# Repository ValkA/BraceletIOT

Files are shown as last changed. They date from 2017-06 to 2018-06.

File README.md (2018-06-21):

# Bracelet 101
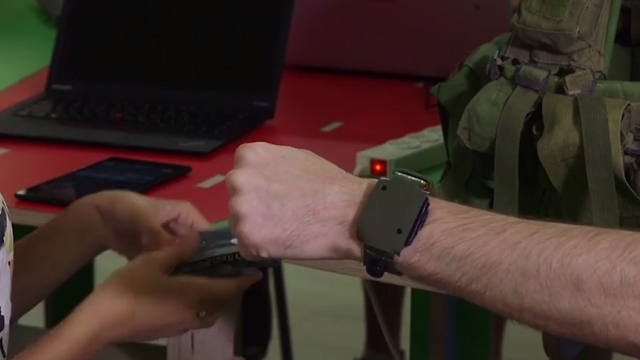
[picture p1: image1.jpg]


This is the repository of "Bracelet 101", a POC of smart bracelet for Medical Corps that is attached to an injured person in order to record medical events (i.e injection of morphine, wearing a tourniquet etc...).

The bracelet uses NFC to register events in the field and Bluetooth to communicate later with an Android device that is held by a doctor at hospital or at the battalion aid station.

Each medical treatment has an NFC tag with the id of the treatment and should be registered in the bracelet by holding it near the bracelet before giving the treatment to the injured person.

## Media:
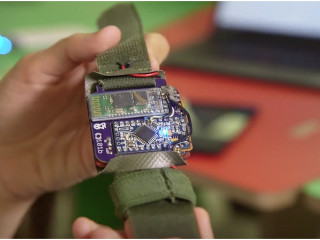
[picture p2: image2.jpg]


Israel Hayom article - http://www.israelhayom.co.il/article/565423/

YNet Health article - https://www.ynet.co.il/articles/0,7340,L-4991215,00.html

Israeli Channel 10 article - http://192.118.60.6/radioMP4/2017/07/25/7880181.mp4

Technion Israel Institute of Technology Facebook page - https://www.facebook.com/Technion.Israel/videos/1805491129468339/

## Bluetooth protocol:
The bracelet reads commands via Bluetooth serial in the format <$type,$data>.

After receiving a command, the bracelet sends '#' as an ack. If there wasn't enough memory to add a record, __the bracelet will send '!' back__, instead of '#'.

The following types can be sent to the bracelet:

- <0,Integer> adds a tag scan. In case the doctor wants to add a treatment manually through the phone.
$data is the treatment number.

- <2,Integer> - adds new data (such as temperature measurement by doctor).

- <3,$time,$tsid,Integer> - update record [$time,$tsid] with new data (Integer 14bit max)

- <4,Integer> - adds a record of headquarters communication (such as evacuation notification),
$data can be any kind of Integer.

- <5,Integer> - adds a record of blood pressure.
$data = blood pressure

- <6,Integer> - Turns on buzzer,
$data has no meaning, but should be some kind of Integer. 0 can be put there.

- <7,$time,$tsid,0> - delete record represented by $time,$tsid.

- <8,Integer> - adds soldierID record. $data should contain the soldier's personal number.

- <13,Integer> - adds soldier status (severity of injury).
$data is id of the status.

For example, the command <1,123> will add a record into the bracelet that represents a new connection by a phone that is represented by the number 123. As a response you will get the database.

#### Special commands:

- LOCATION:
To register location you should send <10,(double/float)latitude><11,(double/float)longitude>
you will see the location when you will send <1,doctor_id>. the location will be among the tags in the container.
for example, [<1,3,0,1><10,32.2343><11,7.23456>]. fields 2 and 3 represent the latitude and longitude.

- SYNC:
<14,Integer> - a special record that can be used to keep the Android and the bracelet in sync.
When the bracelet receives this record, it sends the entire database back, but __does not place this record in it's database__.
The format of the database is the same as in <1, Integer>.
This allows this record to be sent periodically from Android to the bracelet to make sure they are both in sync (for example, every 30 seconds).
Similar to <6, Integer> the $data here has no meaning, but should be some kind of Integer.

- DOCTOR CONNECTION:
<1,Integer> on connection this is the first thing should be sent to the bracelet.
$data represents a unique number of the phone.
As an acknowledgement the bracelet will send back its database with the following format:
[<$type,$time,$tsid,$data>, <$type,$time,$tsid,$data>, ..., <$type,$time,$tsid,$data>]
also the format <3,$time,$tsid,$pointer_time,$pointer_tsid,$data> may be in the container,
which represents an update record (that was added with <3,$time,$tsid,Integer> message from doctor)
(records can be tags, app_data or any other things as defined in this doc https://docs.google.com/document/d/1-qHOoyWK5xLiwJvJ40AK0ONJ1xDmyQk-YbECwnUxzqk/edit)

## NFC Protocol (Tag format):
The tags scanned by the bracelet must be in one of the following 2 formats:
- Integer String

For example: 50 Optalgin 10mg

This format is used for different treatments. It's supposed to be in an NFC tag attached to the treatment item, to be scanned by the bracelet.

- dInteger String

For example: d1234567 Israel Israeli

This format is for the soldier personal number. It's supposed to be in an NFC tag attached to the soldier's tag (diskit).

Notice that in both cases __only the number is scanned by the bracelet__. The following string is completely ignored. It is there __optionally__ so that it could be used in other devices.

The Integer must be smaller than 2^28, which is the maximum number that can be saved in the bracelet (28 bits are stored for each record's data).

## Debugging:
It is possible to send debugging commands to the Arduino through the Serial (physical connection to the PC). There are currently 3 types of debugging commands:
- d - print the current database to the Serial.
- m - print memory information to the Serial (number of records currently stored)
- <$type,$data> - add a specific record to the Arduino. The record would be parsed in the exact same manner as a record sent to the Arduino from Bluetooth. If the record is not recognized as one of the above legal records, you'll get an error and the record would not be added.

The Arduino also sends debugging information to the Serial during normal operation, such as detailed error messages. Therefore, if you encounter unexpected behaviour when interfacing through Bluetooth, connect the Arduino through the serial to see detailed debug messages.

## Wiring:
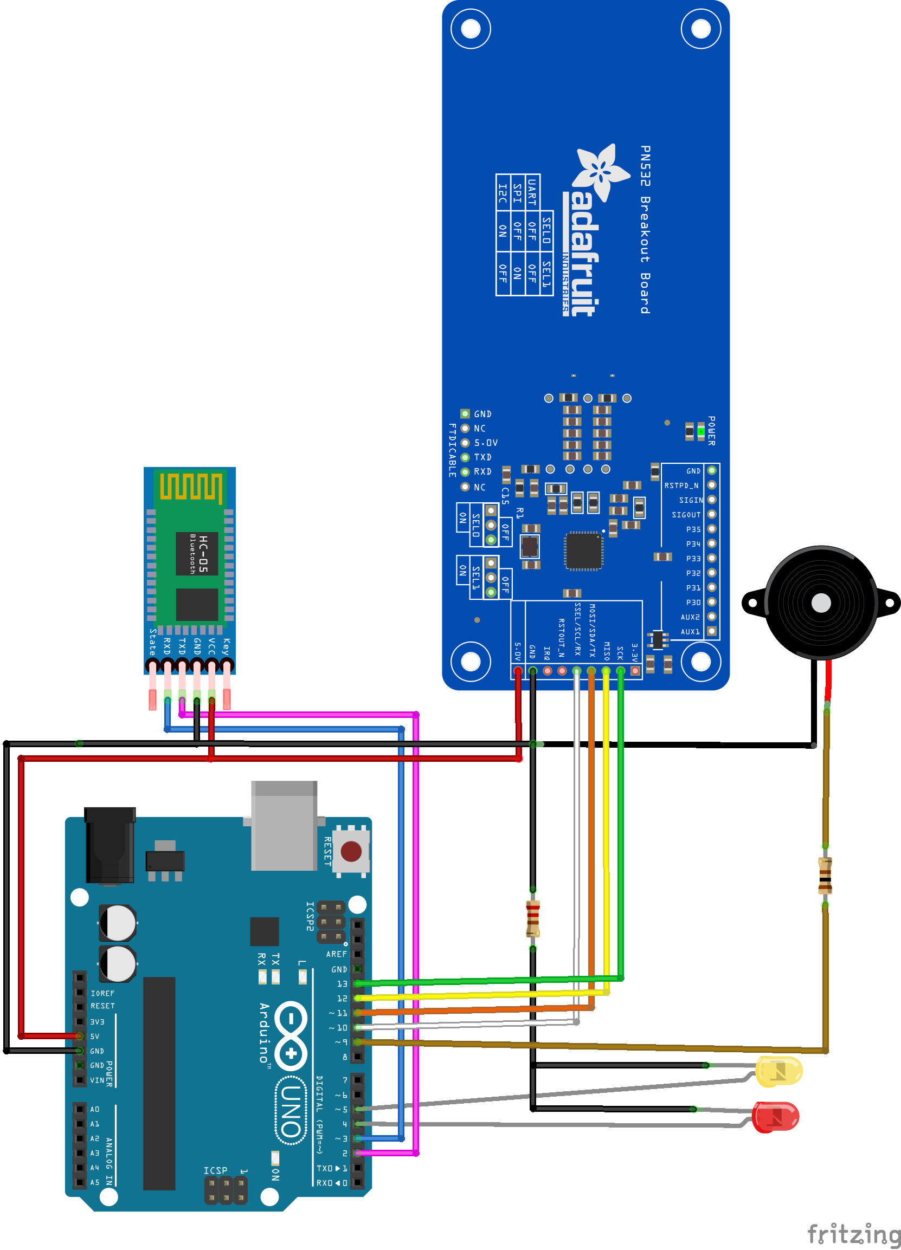
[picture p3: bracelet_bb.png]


## IDE:
Don't forget to include libraries from "Libraries for IDE" folder

## Sounds and LEDs
You can change the buzzer sound or leds light with Bluetooth terminal.
The notes are configured for different cases and you can change configuration for any type separately. The types are:
  TurnOnSuccess = 0,
  TurnOnFailed = 1,
  ScanningSuccess = 2,  
  ScanningFailed = 3,
  ConnectingSuccess = 4,
	NewAppMessage = 5,
	BeepFromApp = 6,
	UnknownTag = 7

The command should starts with '[' and ends with ']'.
For change sound insert:
[0, type, frequency, freqParam , delay,  repeats]

*"type" between 0-7 as explained above.

For example:
[0,2,31,50,200,6] - will change the sound for ScanningSuccess.

For change led i insert: (i={1,2})
[i, type, delayOn,  delayOff,  repeats]

*Delay is in ms.

For example:
[0,2,500,500, 3] - will change the first/second led blinks for ScanningSuccess.

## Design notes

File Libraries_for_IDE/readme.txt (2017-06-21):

Copy everything from this folder into Documents\Arduino\libraries

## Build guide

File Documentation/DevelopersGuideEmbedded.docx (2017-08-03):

Smart Bracelet 101

# Developer’s Guide

# Embedded Team

Michael Lishansky

Valentin Dashinsky

Sapir Cohen

# Table of Contents

Table of Contents 2

Introduction 3

Setup Instructions 4

Hardware 4

Schematic Diagram 5

Drivers 6

Setting up the workspace 6

Project Structure 7

Memory constraints 8

Bluetooth protocol 9

Generic Commands 9

Special commands 10

Tag Format 11

Debugging 12

Sounds and LEDs 13

# Introduction

The objective of this project was to create a prototype for a “smart bracelet” to be used by the IDF medical corps. The Bracelet is fitted to wounded soldiers, and used to scan treatments using NFC. Each treatment has an NFC tag attached, and the tag is scanned and stored by the bracelet.

The bracelet interfaces with an Android app installed on an Android phone or tablet. The interfacing is done using the specific Bluetooth protocol defined in this document.

The primary objective was ease of use. There are no buttons or other control interfaces on the bracelet. All that is required to record a treatment, is to “touch” the bracelet with the treatment item. This allows the medic to focus on treating the wounded, instead of wasting valuable time on recording treatments manually.

The programming language used in this project is C/C++.

Note: the Arduino has no persistent writable memory. This means that all changes, including the tag database, are lost as soon as it is turned off. According to the current design, the tag database would be transferred to an Android device and saved there. If you wish to save the database persistently on the Arduino, a possible solution would be to add an SD card component to the Arduino, and save the database on the SD card.

# Setup Instructions

## Hardware

The hardware is comprised of the following:

- Arduino (MCU)
- PN532 (NFC scanner)
- HC-05 (Bluetooth chip)
- Yellow/Green LED (indicates success)
- Red LED (indicates an error)
- Buzzer (simple speaker that is used to play error/success tones)

Testing was done on Arduino UNO, Arduino Pro Mini and Arduino Nano.

The hardware should be connected as described in the following schematic.

Note: It’s possible to add an NFC tag with the HC-05’s MAC address written inside the tag’s memory (as a string). It is then possible to read that tag using the Android device’s NFC scanner. This will change the screen to the relevant bracelet in the Android app.

This allows the Android user to easily select the bracelet in front of him (instead of sorting through the list of bracelets and trying to find the relevant one), simply by touching it with the Android device.

Important: this attached NFC tag must be located far from the PN532 NFC scanner. Otherwise the scanner will constantly read this tag. Therefore, it is recommended to attach it to the opposite side of the scanner (the “bottom” of the bracelet).

## Schematic Diagram

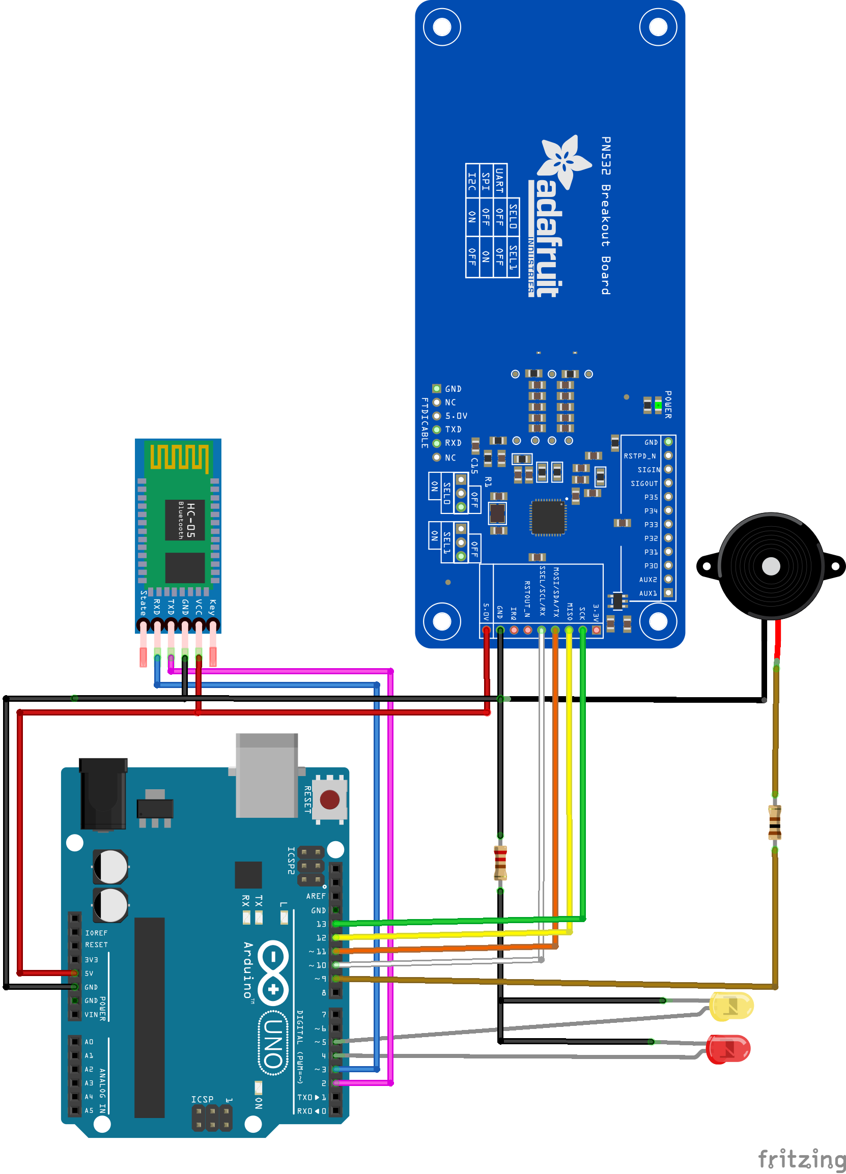
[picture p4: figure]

Note: the pin numbers are the same for all tested Arduino types.

The Fritzing file of this diagram (https://github.com/ValkA/BraceletIOT/blob/master/bracelet.fzz) can be found on the GitHub repo.

## Drivers

The Arduino Uno and Arduino Nano have a USB port, and drivers for them are installed with the Arduino IDE.

The Arduino Pro Mini doesnt have a USB port and needs a USB-Serial converter (for example FTDI), more on that can be found here: http://lab.dejaworks.com/programming-arduino-mini-pro-with-ftdi-usb-to-ttl-serial-converter/

Drivers for FTDI USB-Serial converter can be found here:

http://www.ftdichip.com/Drivers/D2XX.htm

Since the project is hosted on Github in a Git repo, it’s recommended to use Git: https://git-scm.com/

It’s also possible to just download the project files as a zip from the repository: https://github.com/ValkA/BraceletIOT (click on “Clone or Download” -> “Download ZIP”).

## Setting up the workspace

The project was built using Arduino IDE 1.8.2.

1. Download the IDE from here https://www.arduino.cc/en/Main/Software and install it
2. Clone the project ”git clone https://github.com/ValkA/BraceletIOT.git”
3. Copy the NFC libraries from “Libraries_for_IDE” (GitHub repo) into “Documents\Arduino\libraries” (your PC).
4. Open “Bracelet_Arduino/Bracelet_Arduino.ino” with Arduino IDE.
5. Connect the arduino board to USB.
6. From “Tools > Board” choose your board (Mini or Uno).
7. From “Tools > Port” choose the COM Port of your Arduino.
8. Click on the upload button.
9. After compiling and uploading, you should see “Done Uploading” at the bottom.

# Project Structure

The repo can be found here https://github.com/ValkA/BraceletIOT

In the folder “BraceletIOT/Bracelet_Arduino/ (https://github.com/ValkA/BraceletIOT/tree/master/Bracelet_Arduino)“ we have:

- Bracelet_Arduino.ino (https://github.com/ValkA/BraceletIOT/blob/master/Bracelet_Arduino/Bracelet_Arduino.ino) - The “main” file. Contains the setup and main loop functions. It uses the NFC Library and handles the logic of when to listen to the NFC scanner, and when to respond to Bluetooth or Debug commands.
- Logs_Container.h (https://github.com/ValkA/BraceletIOT/blob/master/Bracelet_Arduino/Logs_Container.h) - The main data structure in the project - defines how all information is stored in the Arduino’s limited memory.
- Notes.h (https://github.com/ValkA/BraceletIOT/blob/master/Bracelet_Arduino/Notes.h) - contains defines of various notes frequencies and the Tone structure. Contains the logic for sounds and blinking LEDs.
- Parser.h (https://github.com/ValkA/BraceletIOT/blob/master/Bracelet_Arduino/Parser.h) - contains parsing functions that handle input/output. Parses tag scans as well as the Bluetooth protocol.
- TagReader.h (https://github.com/ValkA/BraceletIOT/blob/master/Bracelet_Arduino/TagReader.h) - contains a class that handles communication with the PN532 NFC scanner.

The folder “/BraceletIOT/Libraries_for_IDE (https://github.com/ValkA/BraceletIOT/tree/master/Libraries_for_IDE)” contains NFC libraries that should be copied to “Documents\Arduino\libraries” in the developer’s PC.

## Memory constraints

The Arduino RAM is comprised of only 2kB, and the objective of this project was to use it for storage. This required some special considerations for memory management.

It’s important to note that the Arduino’s 2kB are also used for function calls on the stack, as well as temporary variables. This means only about 1kB are available for storage. Therefore, it is imperative to reduce the size of each record[^1] stored in the Arduino as much as possible. We settled on the following format:

- 14 bits for the timestamp.
- 4 bits for the record type (allows for 16 types, which are detailed in the next section).
- 28 bits for the data.

For a total of 46 bits per record.

Note that those are bits and not Bytes.

To achieve those goals, we used C Unions and C bitfields liberally. It’s important to acquaint yourself with those concepts before continuing work on this project.

More information can be found in the internal documentation of the Logs_Container.h file.

Note: since this is an embedded project with a very restricted memory pool, it is highly inadvisable to use dynamic memory allocation. Therefore, all memory allocation in this project is static, and is done at boot time.

Currently the bracelet is configured to store a maximum of 100 records. It is possible to edit this defined number in the Logs_Container.h, but higher numbers were not tested and are likely to result in instability.

# Bluetooth protocol

## Generic Commands

The bracelet reads commands from the Bluetooth serial in the format <$type,$data>.

After receiving a command, the bracelet sends '#' as an ack. If there wasn't enough memory to add a record, the bracelet will send '!' back, instead of '#'.

The following record types can be sent to the bracelet:

- <0,Integer> adds a tag scan. In case the doctor wants to add a treatment manually through the Android device. $data is the treatment number.
- <2,Integer> - adds new data (such as temperature measurement by doctor).
- <3,$time,$tsid,Integer> - update record [$time,$tsid] with new data (Integer 14bit max)
- <4,Integer> - adds a record of headquarters communication (such as evacuation notification), $data can be any kind of Integer.
- <5,Integer> - adds a record of blood pressure. $data = blood pressure
- <6,Integer> - Turns on buzzer, $data is not used, but should be some kind of Integer. 0 can be put there.
- <7,$time,$tsid,0> - delete record represented by $time,$tsid.
- <8,Integer> - adds soldierID record. $data should contain the soldier's personal number.
- <13,Integer> - adds soldier status (severity of injury). $data is id of the status.

For example, the command <1,123> will add a record into the bracelet that represents a new connection by an Android device that is represented by the number 123. As a response you will get the records database.

## Special commands

- LOCATION: To register location you should send <10,(double/float)latitude><11,(double/float)longitude> you will see the location when you will send <1,doctor_id>. the location will be among the tags in the container. for example, [<1,3,0,1><10,32.2343><11,7.23456>]. fields 2 and 3 represent the latitude and longitude. Note that Location is comprised of 2 records.
- SYNC: <14,Integer> - a special record that can be used to keep the Android and the bracelet in sync. When the bracelet receives this record, it sends the entire database back, but does not place this record in it's database. The format of the database is the same as in <1, Integer>. This allows this record to be sent periodically from Android to the bracelet to make sure they are both in sync (for example, every 30 seconds). Similar to <6, Integer> the $data here is not used, but should be some kind of Integer.
- DOCTOR CONNECTION: <1,Integer> on connection this is the first thing should be sent to the bracelet. $data represents the unique number of the doctor (could be his personal number). As an acknowledgement the bracelet will send back its database with the following format: [<$type,$time,$tsid,$data>, <$type,$time,$tsid,$data>, ..., <$type,$time,$tsid,$data>] also the format <3,$time,$tsid,$pointer_time,$pointer_tsid,$data> may be in the container, which represents an update record (that was added with <3,$time,$tsid,Integer> message from doctor).

Note: as explained previously, there can be 16 possible message types. Type number 12 is the only one not currently used (type 15 is used internally). If you wish to increase the number of possible message types, it is possible to increase the amount of bits allocated for the “type” field in each record from 4 to 5 (or any other number). This can be done in the Logs_Container.h file.

# Tag Format

The tags scanned by the bracelet must be in one of the following 2 formats:

- Integer String For example: 50 Optalgin 10mg This format is used for different treatments. It's supposed to be in an NFC tag attached to the treatment item, to be scanned by the bracelet.
- dInteger String For example: d1234567 Israel Israeli This format is for the soldier personal number. It's supposed to be in an NFC tag attached to the soldier's tag (diskit).

Notice that in both cases only the number is scanned by the bracelet. The following string is completely ignored. It is there optionally so that it could be used in other devices.

The Integer must be smaller than 2^28, which is the maximum number that can be saved in the bracelet (28 bits are stored for each record's data).

# Debugging

It is possible to send debugging commands to the Arduino through the Arduino Serial (can be accessed via “Tools > Serial Monitor” in the IDE.

There are currently 3 types of debugging commands:

- d - print the current database to the Serial.
- m - print memory information to the Serial (number of records currently stored)
- <$type,$data> - add a specific record to the Arduino. The record would be parsed in the exact same manner as a record sent to the Arduino from Bluetooth.

If the record is not recognized as one of the above legal records, you'll get an error and the record would not be added.

The Arduino also sends debugging information to the Serial during normal operation, such as detailed error messages. Therefore, if you encounter unexpected behaviour when interfacing through Bluetooth, connect the Arduino through the serial to see detailed debug messages.

# Sounds and LEDs

You can change the buzzer sound or LED lights using a Bluetooth terminal.

The notes are configured for different cases and you can change configuration of any type separately.

The types are:

TurnOnSuccess = 0

TurnOnFailed = 1

ScanningSuccess = 2

ScanningFailed = 3

ConnectingSuccess = 4

NewAppMessage = 5

BeepFromApp = 6

UnknownTag = 7

The command should starts with '[' and end with ']'.

To change a sound insert: [0, type, frequency, freqParam , delay, repeats]

*"type" is between 0-7 as explained above.

For example: [0,2,31,50,200,6] - will change the sound for ScanningSuccess.

To change LED i insert: (i={1,2}) [i, type, delayOn, delayOff, repeats]

*Delay is in ms.

For example: [0,2,500,500, 3] - will change the first/second led blinks for ScanningSuccess.

[^1] The next section details the possible types of records. Each command detailed there is stored in the memory (unless specified otherwise) and constitutes a single record (unless specified otherwise).

Smart Bracelet 101

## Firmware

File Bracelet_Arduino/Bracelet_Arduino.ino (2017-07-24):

#include <Wire.h>
#include <SoftwareSerial.h>

#include "SPI.h"
#include "PN532.h"
#include "PN532_SPI.h"

#include "Notes.h"
#include "Parser.h"
#include "Logs_Container.h"
#include "TagReader.h"

//pin defines
#define BUZZER_PIN 9
#define LED1_PIN 5 //success
#define LED2_PIN 4 //error
#define PN532_SS 10
#define PN532_MOSI 11
#define PN532_MISO 12
#define PN532_SCK 13
#define HC_06_TX 2
#define HC_06_RX 3

//timeout defines in milliseconds
#define DELAY_BETWEEN_NFC_READS_TIMEOUT 250
#define TAG_PRESENT_TIMEOUT 500
#define WAIT_FOR_ACK_TIMEOUT 200

//Bracelet will send maximum MAX_REPEATS_WHEN_NO_ACK repeats when ack is not recieved.
#define MAX_REPEATS_WHEN_NO_ACK 2

//Buffers (to avoid allocating memory on the stack, which should be avoided as much as possible):
char tagIDBuffer[TAGID_BUFFER_SIZE] = { 0 };

//Structures
PN532_SPI pn532spi(SPI, PN532_SS);
PN532 nfc(pn532spi);
TagReader nfcReader(nfc);
SoftwareSerial bluetoothSerial(HC_06_TX, HC_06_RX);
Notes note = Notes(BUZZER_PIN, LED1_PIN, LED2_PIN);
//The Databse
LogsContainer tags_cont;


void setup(void) {
	//init serial ports
	Serial.begin(115200);
	bluetoothSerial.begin(9600);

	//init nfc
	nfc.begin();
	//check that the NFC scanner is connected:
	uint32_t versiondata = nfc.getFirmwareVersion();
	if (!versiondata) {
		Serial.print(F("ERROR: No PN53x nfc board!"));
		note.buzzerPlay(ScanningFailed); //Instead of ScanningFailed it's possible to add a special boot failed full buzz here.
		note.led2Play(ScanningFailed);
		while (1); // halt - DOES NOT CONTINUE IF CANT FIND AN NFC SCANNER
	}
	nfc.SAMConfig();

	//init leds and buzzer and play successful boot tone
	pinMode(BUZZER_PIN, OUTPUT);
	note.buzzerPlay(TurnOnSuccess);
	note.led1Play(TurnOnSuccess);

	Serial.println(F("Setup done..."));
}

/*
 * The loop cycles through 3 phases:
 * 1. Waiting for tag on the NFC reader (longest phase, exact time is determined by TAG_PRESENT_TIMEOUT)
 * 2. Checking whether there is a message in the bluetooth buffer.
 * 3. Checking whether there is a debug message on the Serial buffer.
 */
void loop(void) {
	readTag(TAG_PRESENT_TIMEOUT);
	if (bluetoothSerial.available()) {
		switch (bluetoothSerial.peek()) {
		case '[':
			changeNoteSettings(bluetoothSerial);
			break;
		case '<':
			handleDoctorMessage(bluetoothSerial);
			break;
		default:
			handleDoctorMessage(bluetoothSerial);
		}
	}
	if (Serial.available()) {
		handleDebugMessage();
	}
}

void changeNoteSettings(Stream& dataString) {
	uint8_t command = dataString.parseInt();
	NoteType typeNumber = (NoteType)dataString.parseInt();
	uint16_t param1 = dataString.parseInt();
	uint16_t param2 = dataString.parseInt();
	uint8_t param3 = dataString.parseInt();
	uint8_t param4 = dataString.parseInt();
	if (dataString.read() != ']') {
		clearStreamBufferUntilNextMessage(dataString);
	}
	switch (command) {
	case 0: //change buzzer configuration
		note.setToneForNote(typeNumber, param1, param2, param3, param4); //frequncy, freqParam , delay,  repeats
		note.buzzerPlay(typeNumber); //plays buzzer to hear the changes.
		break;
	case 1: //change led1 configuration
		note.setLed1ForNote(typeNumber, param1, param2, param3); //  delayOn,  delayOff,  repeates
		note.led1Play(typeNumber); //plays led to see the changes
		break;
	case 2: //change led2 configuration
		note.setLed2ForNote(typeNumber, param1, param2, param3); //  delayOn,  delayOff,  repeates
		note.led2Play(typeNumber); //plays led to see the changes
		break;
	}
	return;
}

//returns true when there is an error
bool handleRecordError(const LogRecord& record) {
	if (record.type == record_error) {
		Serial.println(F("ERROR: OUT OF MEMORY!"));
		note.buzzerPlay(ScanningFailed); //Instead of ScanningFailed it's possible to add a special memroy full buzz here.
		note.led2Play(ScanningFailed);
		delay(DELAY_BETWEEN_NFC_READS_TIMEOUT);
		return true;
	}
	return false;
}

/**
 * busy wait for nfc tag.
 * if found then reads its data and if valid adds relevant record
 * @param timeout [ms]
 */
void readTag(uint16_t timeout) {
	int16_t success;
	char* pTagIdBuffer = tagIDBuffer;
	//busy wait for tag
	if (nfcReader.tagPresent(timeout)) {
		//tag found now read its data
		success = nfcReader.read(pTagIdBuffer, TAGID_BUFFER_SIZE);
		if (success <= 0) {
			Serial.print(F("ERROR: failed NFC read! "));
			Serial.println(success);
			note.buzzerPlay(ScanningFailed);
			note.led2Play(ScanningFailed);
		}
		else {
			Data tagData;
			Data_Type tagType;
			//its a soldier ID tag
			if (pTagIdBuffer[0] == SOLDIER_ID_START_CHAR) {
				pTagIdBuffer = pTagIdBuffer + 1;
				tagType = soldier_id;
				tagData.rawData = atol((char*)pTagIdBuffer);
			} else { //its a treatment tag
				tagType = tag_scan;
				tagData.tagId = atol((char*)pTagIdBuffer);
			}

			//add the tag record and send it via bluetooth
			LogRecord newRecord = tags_cont.addNewRecord(tagType, tagData);
			if (handleRecordError(newRecord)) {
				return;
			}
			recordAddedDebugMessage(newRecord);
			sendRecordBluetooth(newRecord);
			note.buzzerPlay(ScanningSuccess);
			note.led1Play(ScanningSuccess);

			Serial.print(F("DB Size: "));
			Serial.println(tags_cont.getSize());
		}
		//delay necessary to avoid reading the same NFC Tag twice.
		delay(DELAY_BETWEEN_NFC_READS_TIMEOUT);
		return;
	}
}

/**
 * handles aa message from the doctor (that comes via stream)
 * @param stream - in our case its bluetoothSerial, but can be any stream.
 */
void handleDoctorMessage(Stream& stream) {
	LogRecord logRecord;
	if (stream >> logRecord) {//if there is a valid record
		if (logRecord.type != get_db) {
			logRecord = tags_cont.addNewRecord(logRecord.type, logRecord.data);
			if (!handleRecordError(logRecord)) {
				recordAddedDebugMessage(logRecord);
			}
		}
		//do stuff for relevant logRecord.type
		respondToRecordType(stream, logRecord);
	}
	else {//ERROR, handle it by clearing the buffer until the next '<'
		clearStreamBufferUntilNextMessage(stream);
	}
}

/**
 * handles debug messages (that comes from Serial)
 */
void handleDebugMessage() {
	char c = Serial.peek();
	//handle according to message type (its first char)
	LogRecord debugRecord;
	switch (c) {
	case 'd': //print all the tags:
		Serial << tags_cont;
		break;
	case 'm': //print memory info:
		Serial.print(F("DB Size: "));
		Serial.println(tags_cont.getSize());
		break;
	case 'b': //play buzzer:
		note.buzzerPlay(BeepFromApp);
		break;
	case '<': //add new record manually through the serial:
		if (Serial >> debugRecord) {
			if (debugRecord.type != get_db) {
				debugRecord = tags_cont.addNewRecord(debugRecord);
				if (handleRecordError(debugRecord)) {
					return;
				}
				recordAddedDebugMessage(debugRecord);
			}
			if (debugRecord.type == tag_scan) {
				sendRecordBluetooth(debugRecord); //this is not handled in respondToRecordType.
			}
			respondToRecordType(bluetoothSerial, debugRecord);
		}
		else {
			Serial.println(F("ERROR: Wrong container format!"));
			note.buzzerPlay(ScanningFailed);
			note.led2Play(ScanningFailed);
		}
		break;
	default:
		Serial.println(F("ERROR: Unknown command!"));
		note.buzzerPlay(ScanningFailed);
		note.led2Play(ScanningFailed);
	}
	clearStreamBufferUntilNextMessage(Serial);
}

/**
 * sends log message to bluetooth with ack handling
 * @param newRecord - the record we want to send
 */
void sendRecordBluetooth(LogRecord& newRecord) {
	bluetoothSerial << newRecord;
	bluetoothSerial.println(); //This is needed because HC-06/05 doesnt send unless it gets /n
	bool success = resendIfNoAck(newRecord);
	if (!success) {
		Serial.println(F("ERROR: Did not get ack from Android!"));
	}
	else {
		Serial.println(F("SUCCESS: got ack!"));
	}
}

/**
 * handles acks from Android
 * @param  newRecord - the record we send
 * @return - true iff ack recieved
 */
bool resendIfNoAck(LogRecord& newRecord) {
	for (int i = 0; i < MAX_REPEATS_WHEN_NO_ACK; i++) {
		delay(WAIT_FOR_ACK_TIMEOUT);
		if (bluetoothSerial.read() == '#') {
			return true;
		}
		bluetoothSerial << newRecord;
		bluetoothSerial.println();
	}
	return false;
}

void recordAddedDebugMessage(const LogRecord& newRecord)
{
	Serial.print(F("Added: "));
	Serial << newRecord;
	Serial.println();
}

void respondToRecordType(Stream& stream, LogRecord& logRecord) {
	switch (logRecord.type) {
	case app_command:
		stream.println("#");//Ack
		note.buzzerPlay(BeepFromApp);
		break;
	case mobile_device_id:
		stream << tags_cont;
		note.buzzerPlay(ConnectingSuccess);
		note.led1Play(ConnectingSuccess);
		break;
	case app_location_lat:
		//will beep and send ack after <lon_type, lon>
		break;
	case app_location_lon:
		stream.println("#");//Ack
		note.buzzerPlay(NewAppMessage);
		note.led1Play(NewAppMessage);
		break;
	case record_error:
		stream.println("!");//Error (probably memory full)
		break;
	case get_db:
		stream << tags_cont;
		break;
	default:
		//just a beep that message was recieved
		stream.println("#");//Ack
		note.buzzerPlay(NewAppMessage);
		note.led1Play(NewAppMessage);
		break;
	}
}

void clearStreamBufferUntilNextMessage(Stream& stream) {
	while (stream.available() && (stream.peek() != '<' || stream.peek() != '[')) {
		stream.read();
	}
}

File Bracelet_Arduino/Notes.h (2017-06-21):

#ifndef _NOTES_H
#define _NOTES_H

#include <SoftwareSerial.h>

#define DIFFERENT_NOTES_NUM 8

#define NOTE_B0  31
#define NOTE_C1  33
#define NOTE_CS1 35
#define NOTE_D1  37
#define NOTE_DS1 39
#define NOTE_E1  41
#define NOTE_F1  44
#define NOTE_FS1 46
#define NOTE_G1  49
#define NOTE_GS1 52
#define NOTE_A1  55
#define NOTE_AS1 58
#define NOTE_B1  62
#define NOTE_C2  65
#define NOTE_CS2 69
#define NOTE_D2  73
#define NOTE_DS2 78
#define NOTE_E2  82
#define NOTE_F2  87
#define NOTE_FS2 93
#define NOTE_G2  98
#define NOTE_GS2 104
#define NOTE_A2  110
#define NOTE_AS2 117
#define NOTE_B2  123
#define NOTE_C3  131
#define NOTE_CS3 139
#define NOTE_D3  147
#define NOTE_DS3 156
#define NOTE_E3  165
#define NOTE_F3  175
#define NOTE_FS3 185
#define NOTE_G3  196
#define NOTE_GS3 208
#define NOTE_A3  220
#define NOTE_AS3 233
#define NOTE_B3  247
#define NOTE_C4  262
#define NOTE_CS4 277
#define NOTE_D4  294
#define NOTE_DS4 311
#define NOTE_E4  330
#define NOTE_F4  349
#define NOTE_FS4 370
#define NOTE_G4  392
#define NOTE_GS4 415
#define NOTE_A4  440
#define NOTE_AS4 466
#define NOTE_B4  494
#define NOTE_C5  523
#define NOTE_CS5 554
#define NOTE_D5  587
#define NOTE_DS5 622
#define NOTE_E5  659
#define NOTE_F5  698
#define NOTE_FS5 740
#define NOTE_G5  784
#define NOTE_GS5 831
#define NOTE_A5  880
#define NOTE_AS5 932
#define NOTE_B5  988
#define NOTE_C6  1047
#define NOTE_CS6 1109
#define NOTE_D6  1175
#define NOTE_DS6 1245
#define NOTE_E6  1319
#define NOTE_F6  1397
#define NOTE_FS6 1480
#define NOTE_G6  1568
#define NOTE_GS6 1661
#define NOTE_A6  1760
#define NOTE_AS6 1865
#define NOTE_B6  1976
#define NOTE_C7  2093
#define NOTE_CS7 2217
#define NOTE_D7  2349
#define NOTE_DS7 2489
#define NOTE_E7  2637
#define NOTE_F7  2794
#define NOTE_FS7 2960
#define NOTE_G7  3136
#define NOTE_GS7 3322
#define NOTE_A7  3520
#define NOTE_AS7 3729
#define NOTE_B7  3951
#define NOTE_C8  4186
#define NOTE_CS8 4435
#define NOTE_D8  4699
#define NOTE_DS8 4978

/*Definitions of different cases for play notes(sound or lights)*/
enum NoteType {
	TurnOnSuccess = 0,
	TurnOnFailed = 1,
	ScanningSuccess = 2,
	ScanningFailed = 3,
	ConnectingSuccess = 4,
	NewAppMessage = 5,
	BeepFromApp = 6,
	UnknownTag = 7
};

/*Configuration of 2 leds. Every led has parameters to control the blinks*/
class Leds {
private:
	uint8_t pinLed1;
	uint16_t delayLed1On;
	uint16_t delayLed1Off;
	uint8_t repeatsLed1;
	uint8_t pinLed2;
	uint16_t delayLed2On;
	uint16_t delayLed2Off;
	uint8_t repeatsLed2;
	NoteType type;

public:
	Leds() {};
	Leds(uint8_t led1, uint16_t delay1on, uint16_t delay1off, 
		uint8_t repeats1, uint8_t led2, uint16_t delay2on, 
		uint16_t delay2off, uint8_t repeats2, NoteType type) {
		pinMode(led1, OUTPUT);
		pinMode(led2, OUTPUT);
		this->pinLed1 = led1;
		this->delayLed1On = delay1on;
		this->delayLed1Off = delay1off;
		this->repeatsLed1 = repeats1;
		this->pinLed2 = led2;
		this->delayLed2On = delay2on;
		this->delayLed2Off = delay2off;
		this->repeatsLed2 = repeats2;
		this->type = type;
	}

	void updateLed1(uint8_t delayOn, uint8_t delayOff, uint8_t repeats) {
		this->delayLed1On = delayOn;
		this->delayLed1Off = delayOff;
		this->repeatsLed1 = repeats;
		return;
	}

	void updateLed2(uint8_t delayOn, uint8_t delayOff, uint8_t repeats) {
		this->delayLed2On = delayOn;
		this->delayLed2Off = delayOff;
		this->repeatsLed2 = repeats;
		return;
	}

	void blinkLed1() {
		for (uint8_t i = 0; i < repeatsLed1; i++) {
			digitalWrite(pinLed1, HIGH);
			delay(delayLed1On);
			digitalWrite(pinLed1, LOW);
			delay(delayLed1Off);
		}
		digitalWrite(pinLed1, LOW); //To make sure the led is turnning off.
	}

	void blinkLed2() {
		for (uint8_t i = 0; i < repeatsLed2; i++) {
			digitalWrite(pinLed2, HIGH);
			delay(delayLed2On);
			digitalWrite(pinLed2, LOW);
			delay(delayLed2Off);
		}
		digitalWrite(pinLed2, LOW); //To make sure the led is turnning off.
	}

	NoteType getNoteTypeForLeds() {
		return this->type;
	}
};

/*Buzzer configuration*/
class Tone {
private:
	uint8_t pin;
	uint8_t freq;
	uint8_t freqParam;
	uint8_t delayTime;
	uint8_t repeats;
	NoteType type;
public:
	Tone() {};
	Tone(uint8_t pinNumber, uint8_t frequncy, uint8_t freqParamNumber, uint8_t delay, uint8_t repeatsNumber, NoteType type) {
		this->pin = pinNumber;
		this->freq = frequncy;
		this->freqParam = freqParamNumber;
		this->delayTime = delay;
		this->repeats = repeatsNumber;
		this->type = type;
	}
	void playTone() {
		for (uint8_t i = 0; i < repeats - 1; i++) {
			tone(pin, freq, freqParam);
			delay(delayTime);
		}
		tone(pin, freq, freqParam);
	}
	void updateFrequncy(uint8_t frequncy) {
		this->freq = frequncy;
	}
	void updateFrequncyParam(uint8_t freqParamNumber) {
		this->freqParam = freqParamNumber;
	}
	void updateDelay(uint8_t delay) {
		this->delayTime = delay;
	}
	void updateRepeats(uint8_t repeatsNumber) {
		this->repeats = repeatsNumber;
	}
	NoteType getNoteTypeForBuzzer() {
		return this->type;
	}
};
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

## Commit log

2017-03-27 Pairing via NFC works - we need to do something with the key.
    [NDEF_Maker_v1_08_E 2.xlsm]
2017-03-27 cleaned code, merged Tag reading with NFC Pairing emulation
    [NDEF_Maker_v1_08_E 2.xlsm]
2017-04-03 json works one function to print to sw&hw serial
2017-04-03 print fix (for android app - i removed println so it will work)
2017-04-18 added firtzing
    [bracelet.fzz]
2017-04-30 added bluetooth full support with acks added buzzer for feedback updated README updated firtzing with buzzer
    [bracelet.fzz]
2017-05-10 "hackaton" changes: changed sounds (Tom), added memory printing after each tag scan, some cleanup.
2017-06-03 Added support to play with sounds (buzzer) and lights (leds)
    This feature is supported by Arduino terminal for now.
2017-06-13 Added explanation for configure leds and buzzer from BT terminal.
2017-06-14 fater led blink
2017-06-19 changed beeps and led delays
2017-06-24 updated fritzing added debug success flag
    [bracelet.fzz]
2017-06-24 saved it
    [bracelet.fzz]
